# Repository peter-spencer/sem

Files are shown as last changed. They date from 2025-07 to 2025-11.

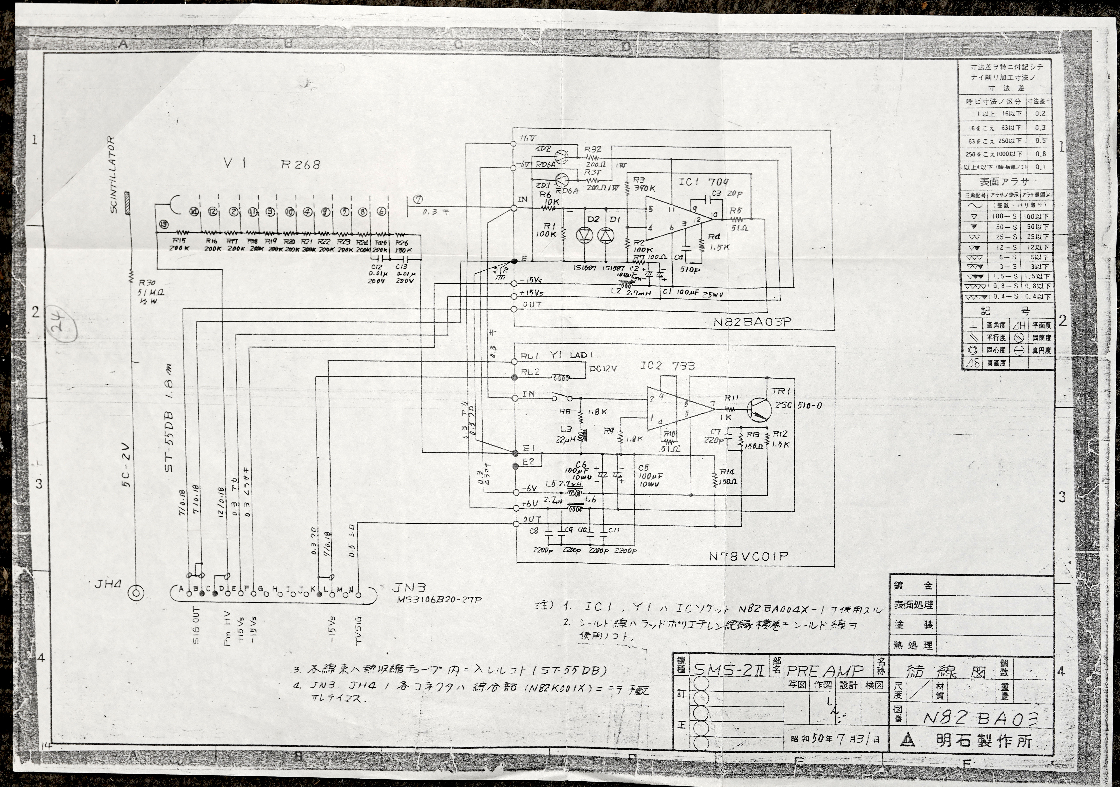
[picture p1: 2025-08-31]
documents/schematics/N82BA03.jpg

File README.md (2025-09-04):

# ISI Super-I Scanning Electron Microscope

The Specimen chamber of the Scanning Electron Microscope

This is a project to restore this old electron microscope and put it back to use again.

So far, the vacuum system, electron column, and specimen chamber has been stripped-down, cleaned and re-assembled. The electronics have been tested and an image was achieved but the old components have suffered several failures.

Currently the focus is to understand and repair the electronics, as well as documenting the whole system for anyone else restorting a similar ISI microscope. There is documentation in the [Wiki](../../wiki).

Hardware will be documented as needed during the refurb, currently there is:
- Scanned user manual and troubleshooting
- [Wiki](../../wiki) with [digitised user manual](../../wiki/Original-Instruction-Manual)
- Scanned original circuit schematics
- A few digitised circuit schematics

A documentary video of this microscope being brought back to life after rescue from storage at the university where it was originally based: https://www.youtube.com/watch?v=1n_eVXKsbxA

## List of related ISI microscopes

There's a comprehensive archive of manuals and schematics for similar ISI microscopes [here in microwiki.org](https://microwiki.org/wiki/index.php/SEM_I-O).

The data in this repository is relevant to the following models of ISI microscopes:

- MSM-4
- SMS-2 Models: Super-I, Super-II, Super-III
- Super Mini SEM

Other ISI microscopes seem to share features with these models and so this list is probably not complete.

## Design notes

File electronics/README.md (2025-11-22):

# SEM Electronics

## Left console

### Switches

1. (Unknown)
2. Scan mode
3. Photo Start
4. (Unknown)
5. (Unknown)
6. Imaging mode (SE, BSE, Spot, Line, etc.)
7. (Gamma control: Not present)
8. (Reduced: Not present)

### Relays

1. Normal or TV Scan (CRT H)
2. Normal or TV Scan (Probe H)
3. CRT Spot killer, ON when AC100V is supplied to console
4. Medium acceleration voltage (magnification)
5. High acceleration voltage (magnification)
6. SCAN MODE: Photo
7. SCAN MODE: Normal
8. SCAN MODE: Rapid 1
9. SCAN MODE: Rapid 2 / TV Scan
10. Normal or Video Amplifier Output

### Potentiometers

1. Front panel: Image Shift X
2. Front panel: Image Shift Y
3. Front panel: Contrast
4. Front panel: Brightness
5. Internal: FOC, CRT Focus
6. Internal: INT, CRT Intensity
7. Front panel: Position X
8. Front panel: Position Y
9. Internal: Line scan adjustment 
10. Internal: Dynamic focus adjustment (not sure what...)

### Circuit boards present

Slot 1 (front): N83ND01P (TV scan horizontal drive?)
Slot 2: N82NC01P (Horizontal scan generator)
Slot 3: N82NB01P^-1^ (Vertical scan generator and signal amplifiers)
Slot 4: N80NA01 (Probe and CRT Scan board)
Slot 5: Unused, no connector
Behind slots (rear of case): N82NH01P (CRT high voltage supply?)
Behind slots (side of case): N82NG01P (Divide by 4 logic)
On top of slots (enclosed): N82NE01P (Video amplifier?)
On top of slots (open): ???

### Connectors present

JN1: Scanning and Shift coils on Electron Column
JN2: Power supply and accelerating voltage logic (indication, not control)
JN3: Electron Detector PMT bias, amplifier, and signal
JN4: High voltage control, and supply, for Electron Detector (and some HV for CRT)
JN5: CRT High Voltage (Special 75 Ohm HN connector, connect to JHB2 or JHB3 on dry HV unit, +10 kV?)
JN6: Photo CRT power supplies, blanking logic, and signal (connect to JPC1)
JN7: To TV scan !?!??! really?
L.P.: Line profile (X-Ray ?)
PULSE AMP.: Preamp for X-Ray ?

## Right console

### Connectors present

JM1: 100 Volt AC power input
(JM2) R.P.: Roughing pump 100 Volt AC power
Valve: AC Power output to optional automatic valve?
JM3: Electron Column and Vacuum (Condenser lenses, Objective lens, Stigmators, Diffusion Pump and Pirani gauge)
JM4: Power supplies OUT, Emission control and gauge, accelerating voltage logic (indication not control)

JPC1: Photo CRT power supplies, blanking logic, and signal
JPC2: Photo CRT High Voltage (Special 75 Ohm HN connector, connect to JHB2 or JHB3 on dry HV unit, +10 kV?)

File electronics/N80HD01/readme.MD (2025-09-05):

# N80HD01

## Regulated power supply and high-voltage drive

This board provides regulated power supplies for the high-voltage drive circuits and also includes part of the high-voltage drive circuit for the CRT displays and the Scintillator detector.

## Power supply specifications

|Voltage|Current|Purpose|Notes|
|---|---|---|---|
|+15 Volts|Output transistor 3.5 Amps emitter current|Positive rail for HV drives| |
|-15 Volts|Output transistor 3.3 Amps emitter current|Negative rail for HV drives| |
|+70 Volts|2 Amps (fused F2-1,F2-2)|HV drive power|75 Volts on some schematics|

## Issues, fixes and upgrades

### Current status

- L1 33uH has been removed some time in the past.
- ZD11 RD6A removed (failed).
- ZD4 RD6A removed (tested OK).
- TR4, TR5, TR6 2SC484-Y removed (failed).
- IC2 741 removed (not tested).

- TR3 2SC484-X removed (failed).
- R15, R16 10k removed (tested OK). Removed to test 70 Volt supply in isolation.

### +70 Volt power supply

The +70 Volt power supply failed after the problems with the high-voltage (oil) unit and it was left outputting the ~90 Volts unregulated supply voltage.

The simulations showed that there is a design issue with the output transistor triplet: Under heavier loads, the collector current in middle transistor of the triplet (TR6) can rise to be equal to the collector current of the final transistor (off-board in the dry high voltage unit). TR6 is not rated for these currents and has no provision for dissipating the Watts of heat generated.

Overloading of TR6 will occur before either of the 1 Amp fuses would normally blow and this is probably what caused the failures of TR4,5,6 and ZD11.

The solution I am going to try is to replace the output transistor with a Darlington NPN that is rated to handle the 90 Volt unregulated supply voltage with a reasonable margin for error. TR5 and TR6 will be bypassed and removed.

In simulation this seems to completely resolve the issues with overloading before the fuses could blow.

### ±15 Volt power supply

No problems with this supply have been found yet and the simulation suggests that the current circuit works well enough. Modern regulator chips such as a 7815 and 7915 pair will probably perform at least as well if not better and so should be considered as a replacement if this supply fails in future.

### High voltage driver for Scintillator and CRTs

I suspect that this may have been damaged by the +70V supply failure: **To be determined**.

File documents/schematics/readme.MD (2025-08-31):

# Circuit schematics

Models of electron microscope with data here:

- **N78** MSM-4 (modules re-used in SMS-2)
- **N80** SMS-2
- **N81** SMS-2I
- **N82** SMS-2II

The majority of the schematics are for the SMS-2 (N80), a few for the SMS-2II (N82), and a handful for the other models.

|Drawing|Model|Location|Description|
|---|---|---|---|
|N78B12|MSM-4, SMS-2|Specimen chamber|Scintillator detector and preamplifier|
|N78NC01|MSM-4, SMS-2|Photo CRT sub-unit|Photo CRT scan amplifiers|
|N78PC01|MSM-4, SMS-2|Right section of display console|Photo CRT sub-unit|
|N80H04|SMS-2|High voltage (dry)|Unit|
|N80HA13|SMS-2|High voltage (oil)|Unit|
|N80HB01|SMS-2|High voltage (dry)|Scintillator and CRT high voltage supply|
|N80HB01|SMS-2|High voltage (dry)|Scintillator and CRT high voltage supply (with highlighter)|
|N80HC01|SMS-2|High voltage (dry)|Electron gun and filament high voltage drivers and feedback|
|N80HD01|SMS-2|High voltage (dry)|±15V, +70V regulated power supplies, Scintillator high voltage driver and feedback|
|N80K04|SMS-2|N/A|Whole system|
|N80M01|SMS-2|Left section of display console|Unit|
|N80MA01|SMS-2|Left section of display console|Pirani vacuum gauge and interlock, ±15V regulated power supply, probe beam alignment amplifiers|
|N80MB01|SMS-2|Left section of display console|Stigmator and lens amplifiers|
|N80N07|SMS-2|Right section of display console|Unit|
|N80NA01|SMS-2|Right section of display console|Probe and CRT scan|
|N80NB01|SMS-2|Right section of display console|Horizontal sweep and image amplifier|
|N80NC01|SMS-2|Right section of display console|Vertical sweep|
|N81NE01|SMS-2II||One shot indicator|
|N82BA03|SMS-2I||Scintillator detector and preamplifier|
|N82H01|SMS-2II||High voltage (dry)|
|N82NE01|SMS-2II||TV video amplifier|
|N82NG0|SMS-2II||Divide by 4|
|N82NH01|SMS-2II||TV horizontal sweep|

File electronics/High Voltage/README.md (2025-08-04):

# High Voltage System

Working out how the acceleration voltage and filament drive work in detail.

The KiCad schematic file contains all the circuits directly involved in controlling the Acceleration Voltage and Filament Current, including the read-out of Emission Current.

The LTSpice simulation file contains a simplified model of the oscillator and a part of the driver circuit that I made to check that I had correctly understood them.

I've included detail from the front-panel switches through to the emission current read-out to fully understand how the complete system functions.

The oscillator is sensitive to the selection of its Op-Amp component: The schematics show a 709 Op-Amp which is very obsolete and so it's not clear how this could be replaced if it was faulty.

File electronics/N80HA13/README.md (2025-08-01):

# N80HA13

## Oil-Filled High Voltage Unit

This unit generates the acceleration voltage and filament current for the Electron Gun.

Need to add annotations from original schematic and table of values for R4,R5,R6.

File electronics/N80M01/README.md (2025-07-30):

# N80M01

## Power supply control (right console)

This schematic cover the right hand console's front panel controls and some of the internal power supply.

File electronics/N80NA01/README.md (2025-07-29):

# PCB N80NA01

## Probe and CRT Scan board

This PCB appears to contain the amplifiers that drive the high voltage sections responsible for scanning the main electron beam and the CRT display. Investigating this board because the X and Y adjustments of the image are having no effect and the troubleshooting guide points to the Op-amp IC2 (U2).

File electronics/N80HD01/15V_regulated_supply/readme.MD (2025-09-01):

# ±15 Volt regulated power supply

This is a SPICE simulation of the +70 Volt regulated supply.

The circuit does not appear to have any issues.

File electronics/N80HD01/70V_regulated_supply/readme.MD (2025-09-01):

# 70 Volt regulated supply simulation

This is a SPICE simulation of the +70 Volt regulated supply for troubleshooting purposes.

It has been able to diagnose that TR6 can be overloaded and burn-out before the protection fuses (2x 1 Amp in the dry high voltage unit) blow.

Replacing the off-board output transistor with a Darlington NPN rated for the full load, and bypassing TR5 and TR6, appears to be good solution.

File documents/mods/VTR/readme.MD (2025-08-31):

# Video Tape Recorder (VTR) Modification

This modification is for Super II, Super IIa, Super IIb microscopes and is to be used with the TVscan add-on unit.

The instructions detail how to install a connector for outputting the TV signal and horizontal/vertical blanking signals and ±15 Volts power supply, as well some minor modifications to the existing circuits for compatibility.

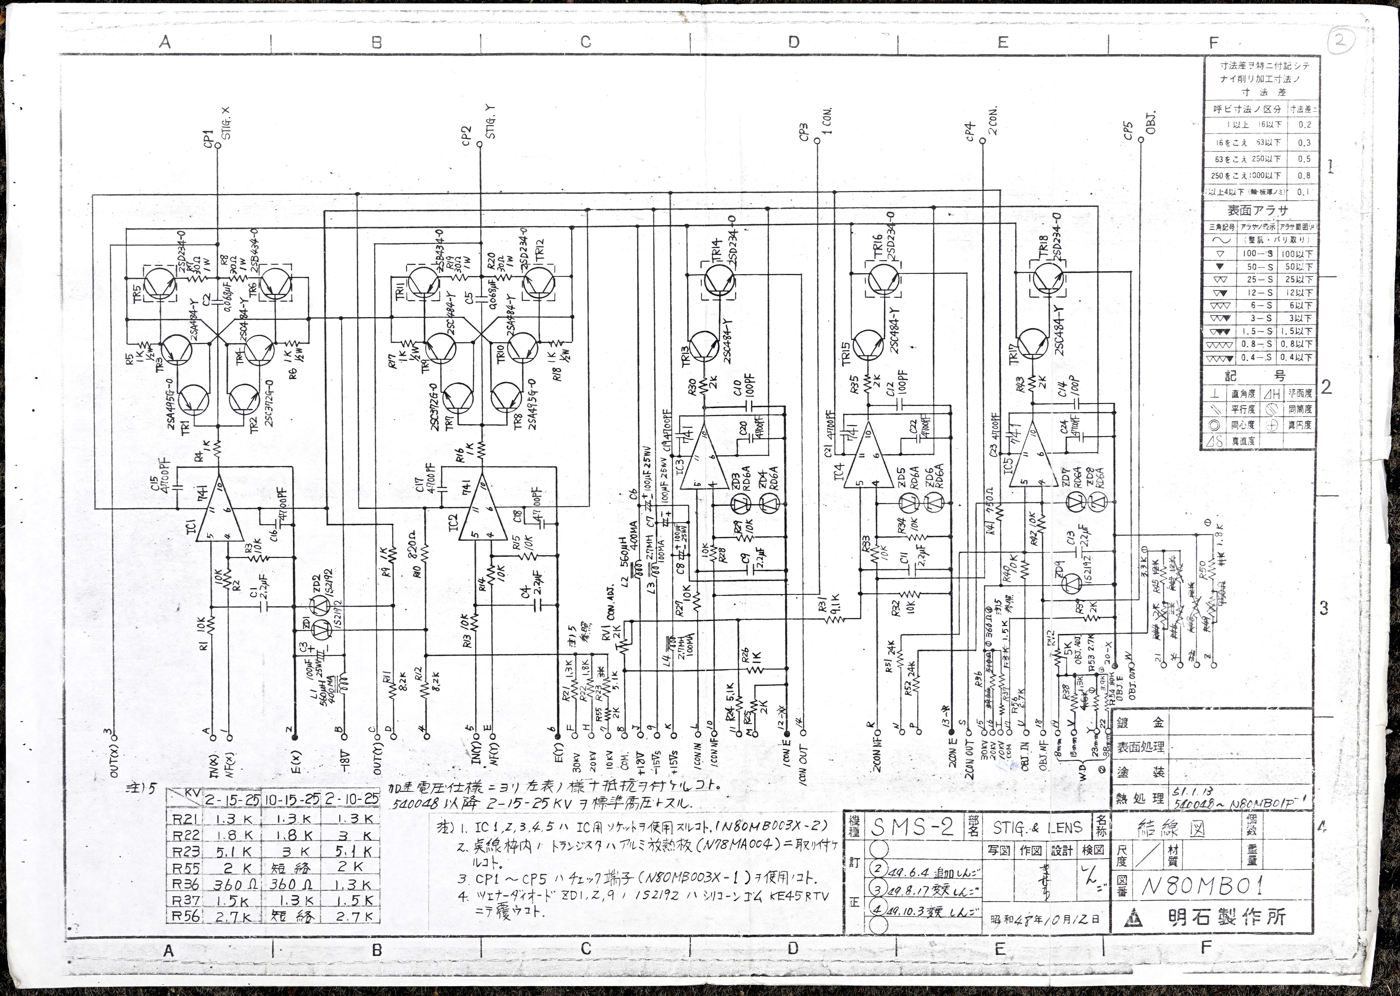
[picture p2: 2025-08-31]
documents/schematics/N80MB01.jpg

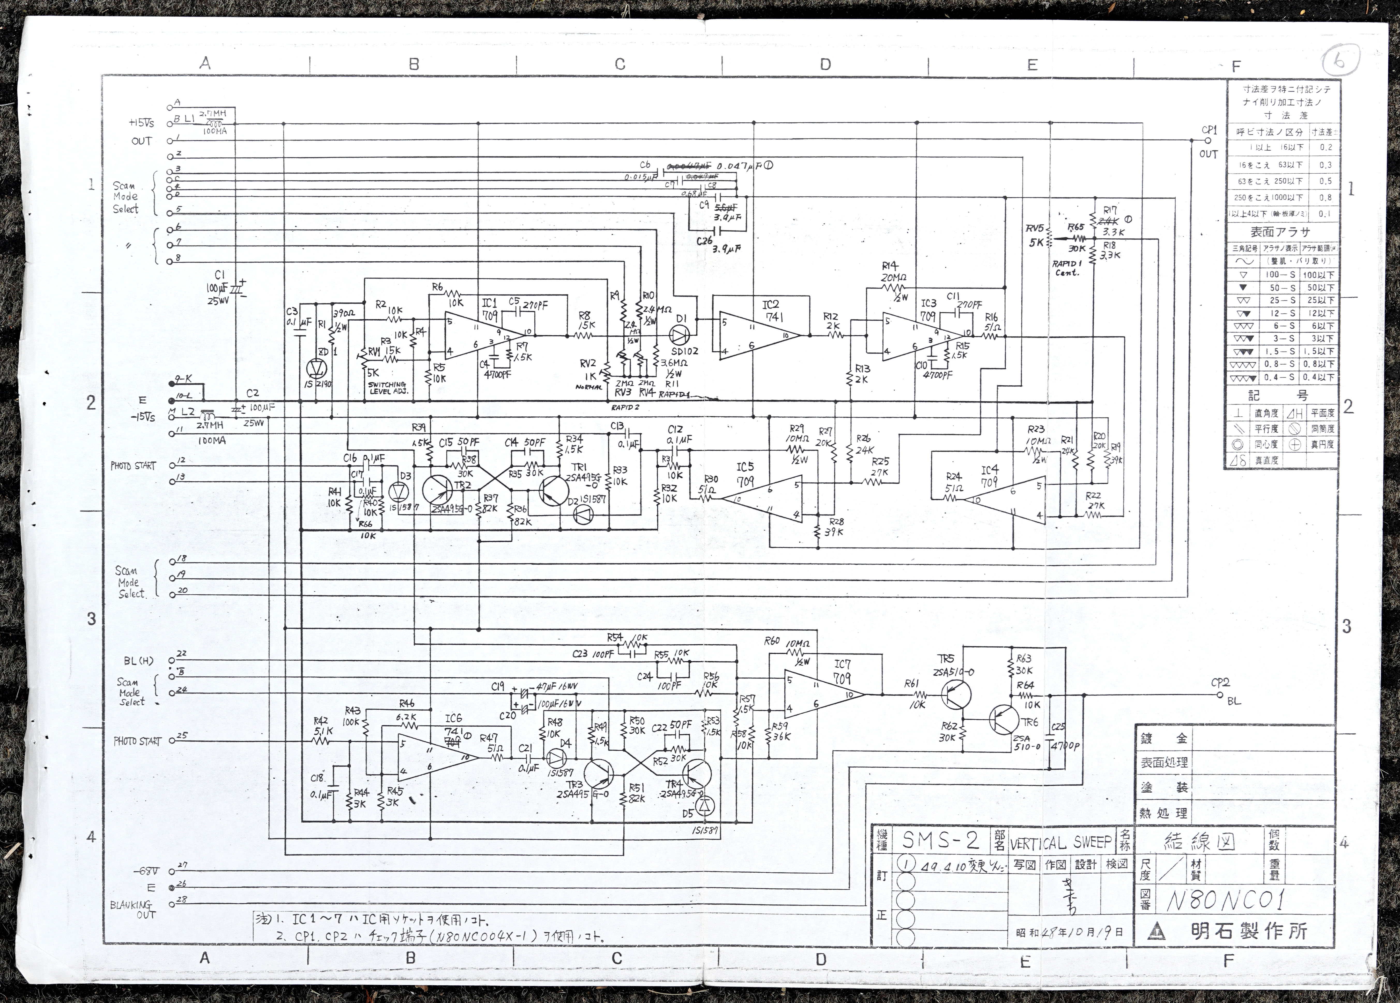
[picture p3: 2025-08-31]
documents/schematics/N80NC01.jpg

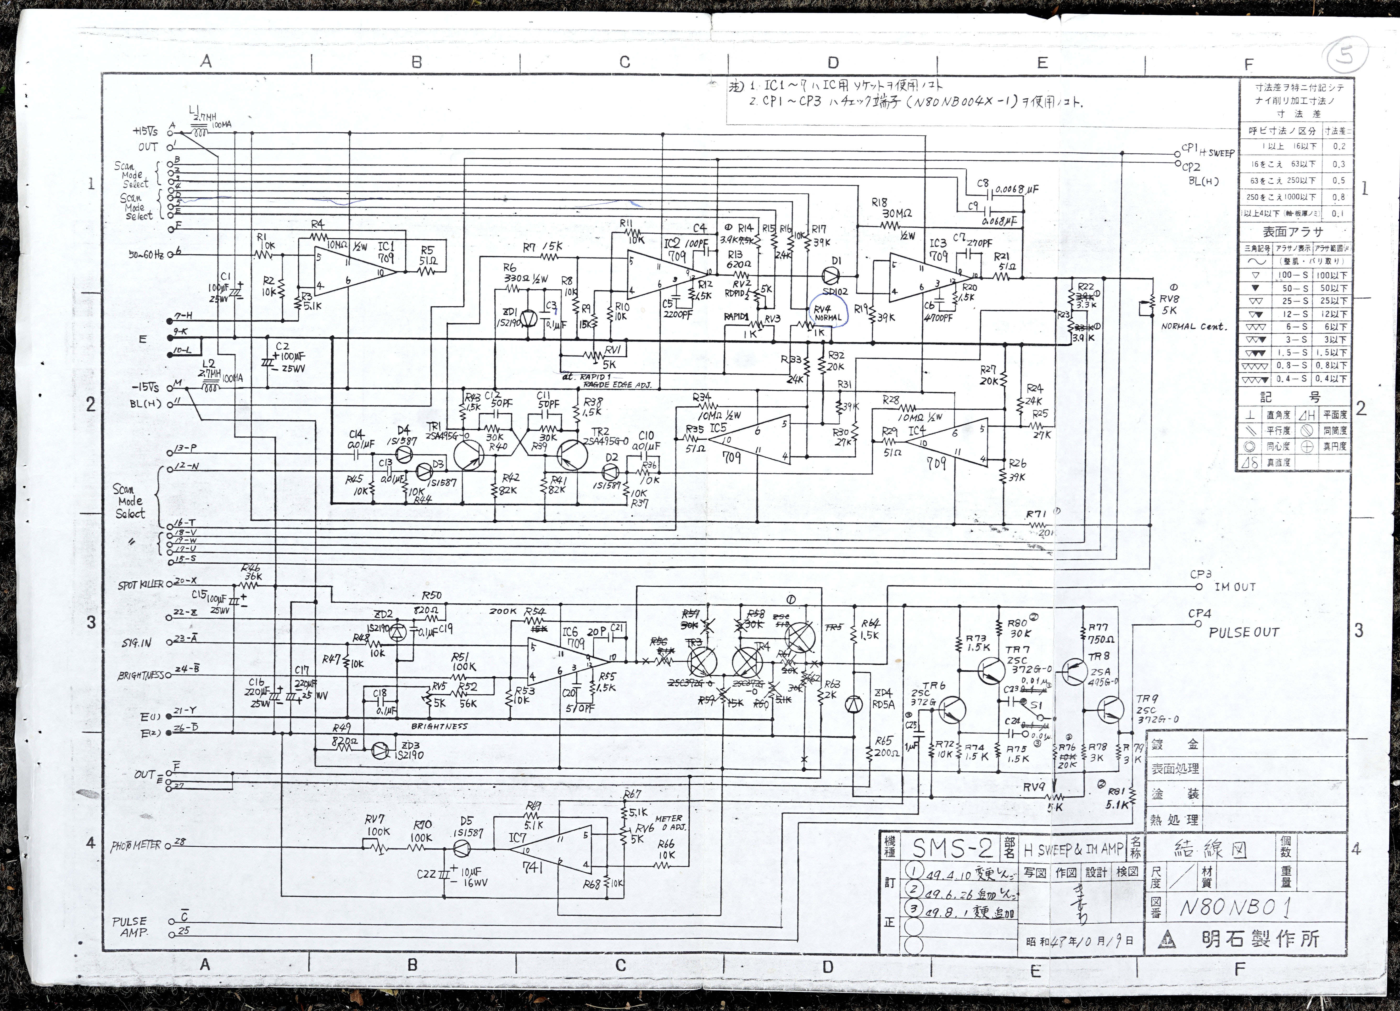
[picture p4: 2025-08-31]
documents/schematics/N80NB01.jpg

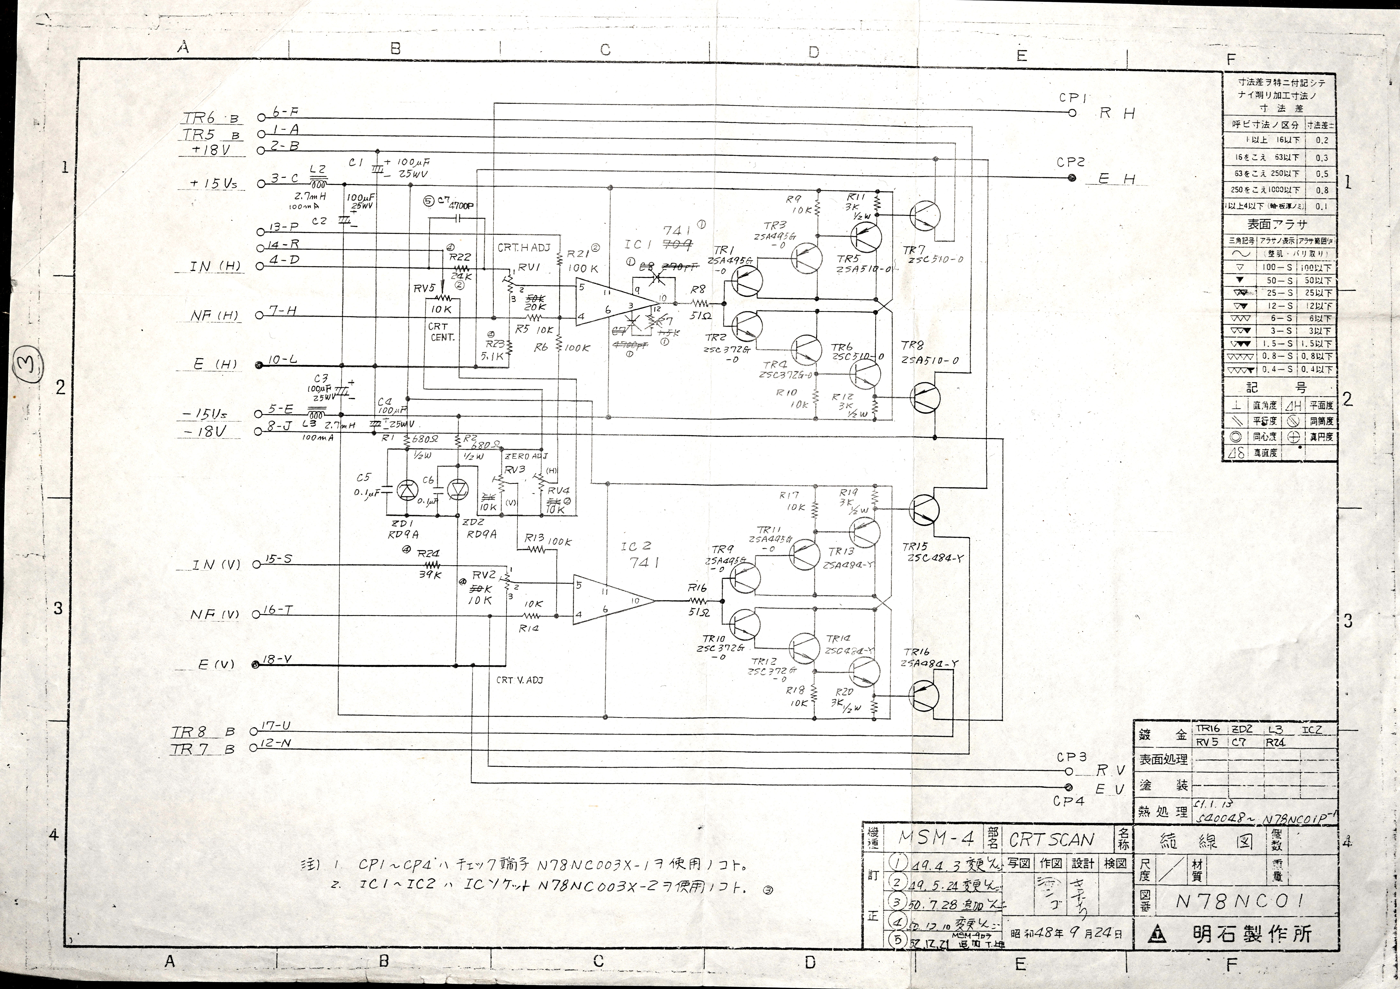
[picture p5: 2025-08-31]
documents/schematics/N78NC01.jpg

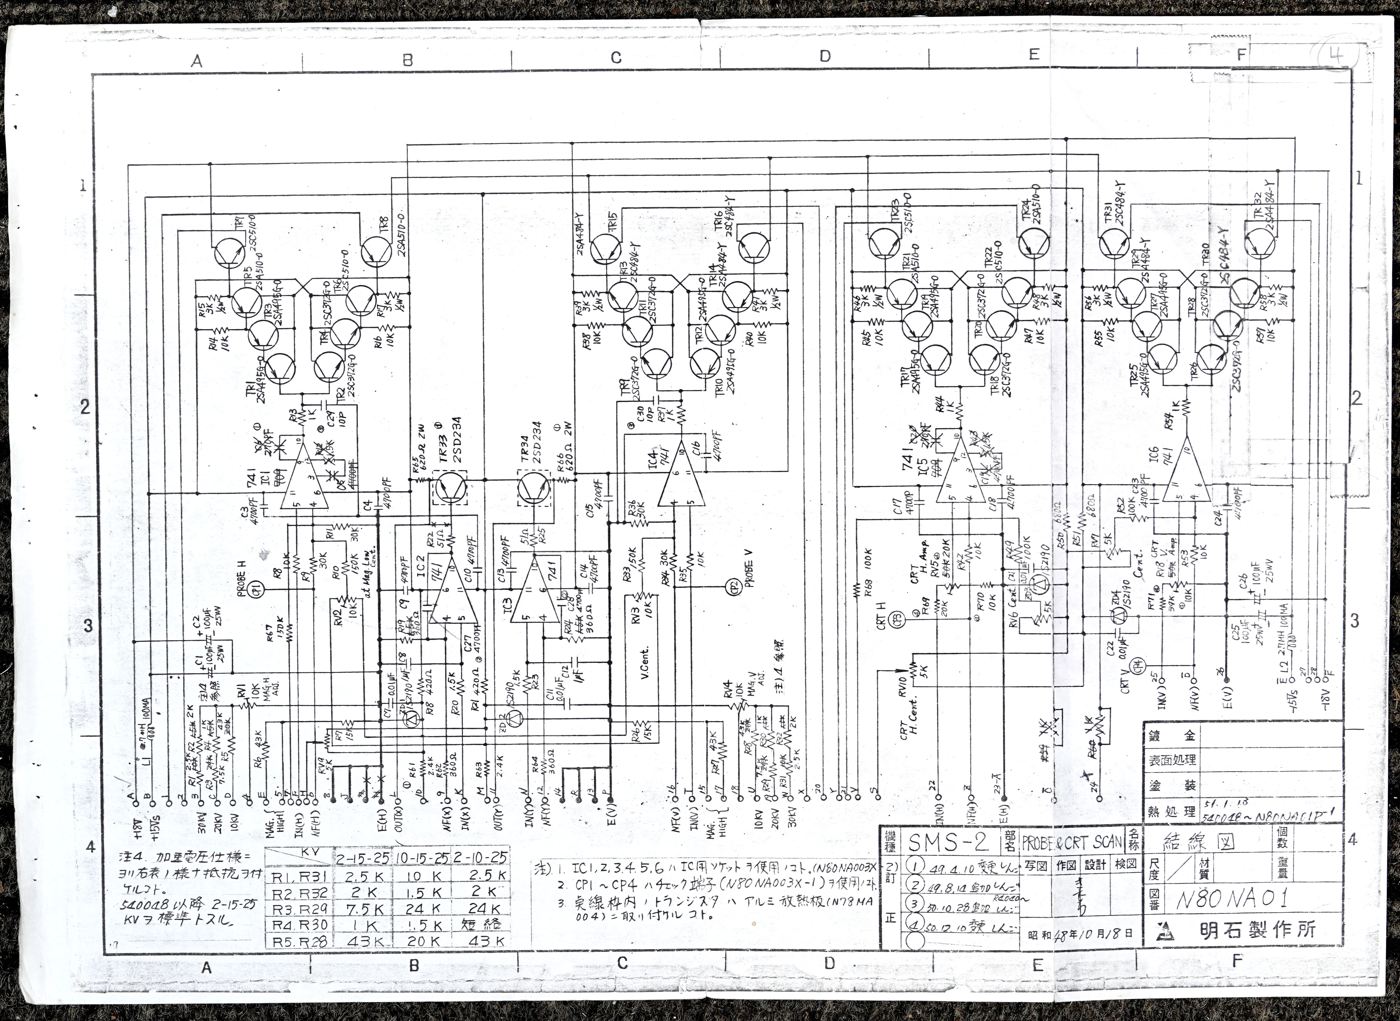
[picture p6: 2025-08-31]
documents/schematics/N80NA01.jpg

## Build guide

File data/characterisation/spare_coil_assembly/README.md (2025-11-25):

# Frequency response of the spare SEM coil assembly

There was a spare coil assembly included in the accessories that came with the SEM, this is the results of measuring the coils.

## Setup

Signal generator with 50 Ohm output impedance was then connected to the coil under test in series with a 10 kilohm resistor. The terminal of the coil under test that was connected to the signal generator was the 0 Volt earth.

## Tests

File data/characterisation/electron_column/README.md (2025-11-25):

# Frequency response of the SEM coils

## Setup

Signal generator with 50 Ohm output impedance was then connected to the coil under test in series with a 10 kilohm resistor. The terminal of the coil under test that was connected to the signal generator was the 0 Volt earth.

For the shielding test, the shield wire was connected to the same earth as the coil under test.

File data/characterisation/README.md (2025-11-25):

# Characterisation Data

This folder contains experimentally measured empirical data that describes the performance of the SEM.
#

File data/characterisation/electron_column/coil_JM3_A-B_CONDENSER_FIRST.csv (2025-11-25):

# | Frequency (Hz) | Amplitude (Vpp) | Gain (dB) | Phase (°)
1 | 100.0 | 0.0500 | -50.01 | 53.33
2 | 101.2 | 0.0500 | -49.90 | 50.27
3 | 102.3 | 0.0500 | -49.99 | 53.23
4 | 103.5 | 0.0500 | -49.57 | 51.30
5 | 104.7 | 0.0500 | -49.53 | 52.76
6 | 105.9 | 0.0500 | -49.57 | 53.87
7 | 107.2 | 0.0500 | -49.54 | 52.82
8 | 108.4 | 0.0500 | -49.54 | 54.21
9 | 109.6 | 0.0500 | -49.48 | 53.30
10 | 110.9 | 0.0500 | -49.35 | 53.13
11 | 112.2 | 0.0500 | -49.53 | 52.99
12 | 113.5 | 0.0500 | -49.41 | 53.41
13 | 114.8 | 0.0500 | -49.28 | 54.05
14 | 116.1 | 0.0500 | -49.07 | 52.42
15 | 117.5 | 0.0500 | -49.48 | 52.49
16 | 118.9 | 0.0500 | -49.39 | 53.11
17 | 120.2 | 0.0500 | -49.22 | 53.93
18 | 121.6 | 0.0500 | -49.08 | 54.45
19 | 123.0 | 0.0500 | -48.97 | 52.42
20 | 124.5 | 0.0500 | -48.63 | 52.40
21 | 125.9 | 0.0500 | -48.81 | 52.64
22 | 127.4 | 0.0500 | -48.85 | 53.30
23 | 128.8 | 0.0500 | -48.82 | 51.20
24 | 130.3 | 0.0500 | -48.85 | 54.16
25 | 131.8 | 0.0500 | -48.83 | 52.38
26 | 133.4 | 0.0500 | -48.53 | 53.72
27 | 134.9 | 0.0500 | -48.56 | 52.14
28 | 136.5 | 0.0500 | -48.58 | 54.01
29 | 138.0 | 0.0500 | -48.60 | 53.34
30 | 139.6 | 0.0500 | -48.30 | 52.95
31 | 141.3 | 0.0500 | -48.22 | 52.60
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

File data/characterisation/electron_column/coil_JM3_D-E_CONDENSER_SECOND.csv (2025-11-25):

# | Frequency (Hz) | Amplitude (Vpp) | Gain (dB) | Phase (°)
1 | 100.0 | 0.0500 | -49.90 | 52.57
2 | 101.2 | 0.0500 | -49.88 | 51.15
3 | 102.3 | 0.0500 | -49.71 | 53.66
4 | 103.5 | 0.0500 | -49.74 | 53.02
5 | 104.7 | 0.0500 | -50.06 | 51.09
6 | 105.9 | 0.0500 | -49.73 | 51.72
7 | 107.2 | 0.0500 | -49.82 | 55.15
8 | 108.4 | 0.0500 | -49.61 | 52.63
9 | 109.6 | 0.0500 | -49.38 | 52.84
10 | 110.9 | 0.0500 | -49.45 | 54.25
11 | 112.2 | 0.0500 | -49.57 | 52.31
12 | 113.5 | 0.0500 | -49.39 | 53.41
13 | 114.8 | 0.0500 | -49.52 | 52.63
14 | 116.1 | 0.0500 | -49.41 | 54.25
15 | 117.5 | 0.0500 | -49.42 | 54.12
16 | 118.9 | 0.0500 | -49.22 | 54.07
17 | 120.2 | 0.0500 | -49.34 | 52.75
18 | 121.6 | 0.0500 | -49.15 | 52.65
19 | 123.0 | 0.0500 | -49.12 | 54.25
20 | 124.5 | 0.0500 | -49.07 | 53.19
21 | 125.9 | 0.0500 | -49.00 | 52.25
22 | 127.4 | 0.0500 | -48.96 | 53.29
23 | 128.8 | 0.0500 | -49.08 | 52.83
24 | 130.3 | 0.0500 | -48.72 | 52.55
25 | 131.8 | 0.0500 | -48.71 | 53.54
26 | 133.4 | 0.0500 | -48.64 | 52.38
27 | 134.9 | 0.0500 | -48.63 | 52.55
28 | 136.5 | 0.0500 | -48.70 | 53.86
29 | 138.0 | 0.0500 | -48.62 | 51.85
30 | 139.6 | 0.0500 | -48.34 | 52.17
31 | 141.3 | 0.0500 | -48.50 | 52.58
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

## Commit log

2025-07-29 Added N80NA01 Probe & CRT Scan board
    [N80NA01.kicad_pcb, N80NA01.kicad_sch]
2025-07-29 Updated N80NA01 board
    [N80NA01.kicad_sch]
2025-07-30 Started adding power supplies
    [N80M01.kicad_pcb, N80M01.kicad_sch, N80M01_power.kicad_sch, N80MA01P.kicad_sch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]
2025-07-30 Added more detail to Probe & CRT drive schematic
    [CRT_H.kicad_sch, CRT_V.kicad_sch, IMAGE_SHIFT_X.kicad_sch, IMAGE_SHIFT_Y.kicad_sch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]
2025-08-01 Updated the probe driver schematics
    [N80NA01.kicad_sch, PROBE_H.kicad_sch, PROBE_V.kicad_sch]
2025-08-01 Added schematic for Oil-Filled HV unit
    [N80HA13.kicad_pcb, N80HA13.kicad_sch, high_voltage.kicad_pcb, high_voltage.kicad_sch]
2025-08-02 Added Dry HV electron gun circuit
    [high_voltage.kicad_sch]
2025-08-02 Completed EG parts of N80H04
    [high_voltage.kicad_sch]
2025-08-02 Added N80HC01 to High Voltage
    [high_voltage.kicad_sch]
2025-08-02 Added all circuits to the High Voltage schematic
    [high_voltage.kicad_sch]
2025-08-03 EG filament and notes added
    [high_voltage.kicad_sch]
2025-08-04 Corrections to HV driver operation
    [high_voltage.kicad_sch]
2025-08-26 Adding dry HV power supply N80HD01
    [70V_regulated_supply.kicad_pcb, 70V_regulated_supply.kicad_sch]
2025-08-31 Working on 70 Volt supply for HV
    [70V_regulated_supply.kicad_sch]
2025-09-01 Added ±15V psu simulation and gitignore
    [15V_regulated_supply.kicad_pcb, 15V_regulated_supply.kicad_sch, 70V_regulated_supply.kicad_pcb, 70V_regulated_supply.kicad_sch]
2025-09-01 Update front page
    [15V_regulated_supply.kicad_sch]
2025-11-25 Empirically characterised the coils in the electron column
    [coil_JM3_A-B_CONDENSER_FIRST.csv, coil_JM3_D-E_CONDENSER_SECOND.csv, coil_JM3_G-H_ALIGN_X.csv, coil_JM3_G-H_ALIGN_X_wrong.csv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]
